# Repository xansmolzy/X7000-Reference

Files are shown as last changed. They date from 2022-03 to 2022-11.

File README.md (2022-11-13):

# X7000-Reference
Wavetek 7000 inspired voltage reference on the cheap.
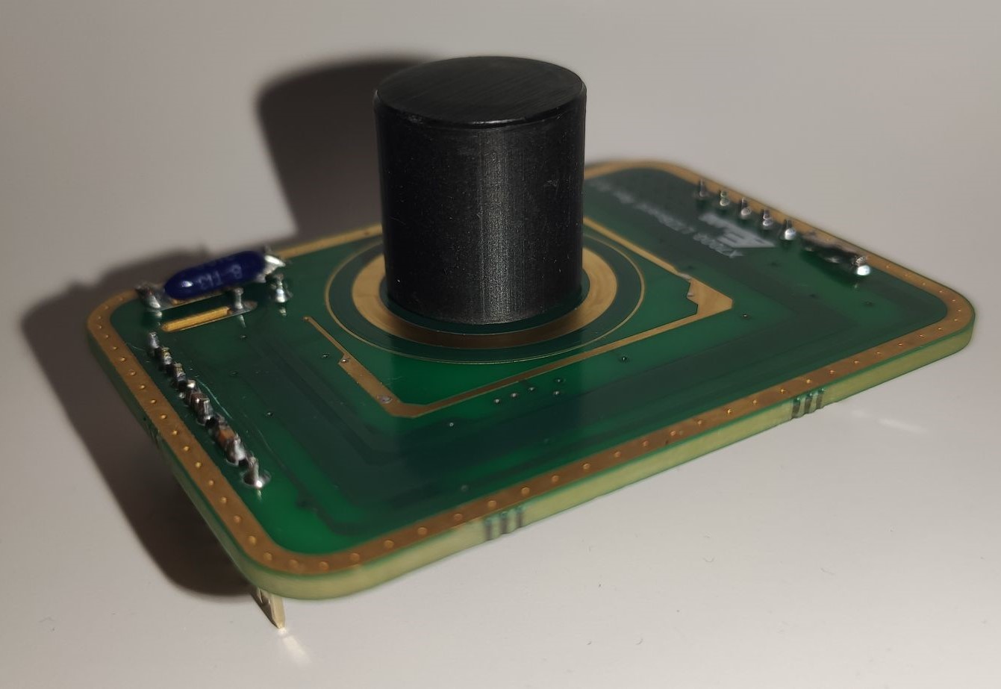
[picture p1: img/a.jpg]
Refpic1
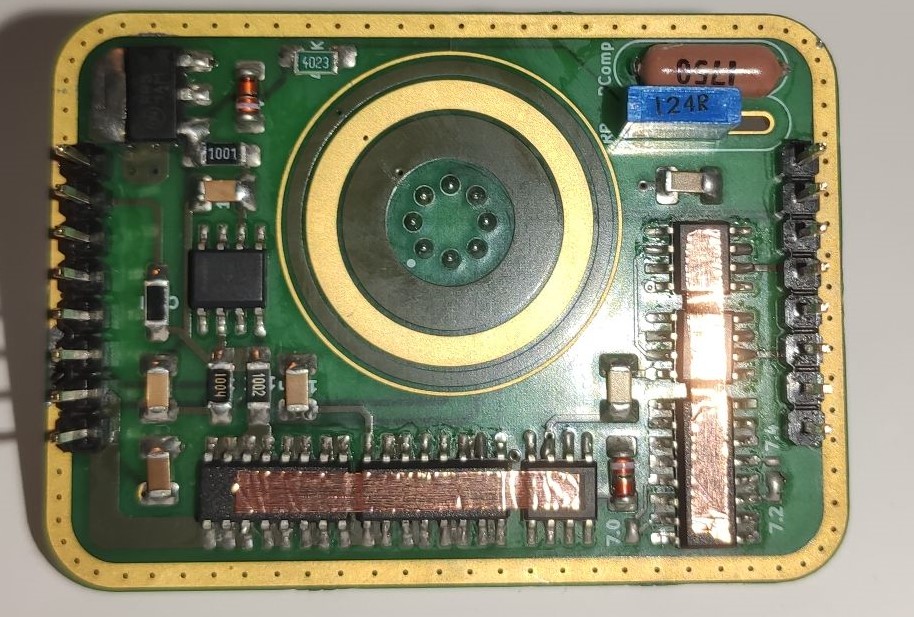
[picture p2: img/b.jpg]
Refpicé
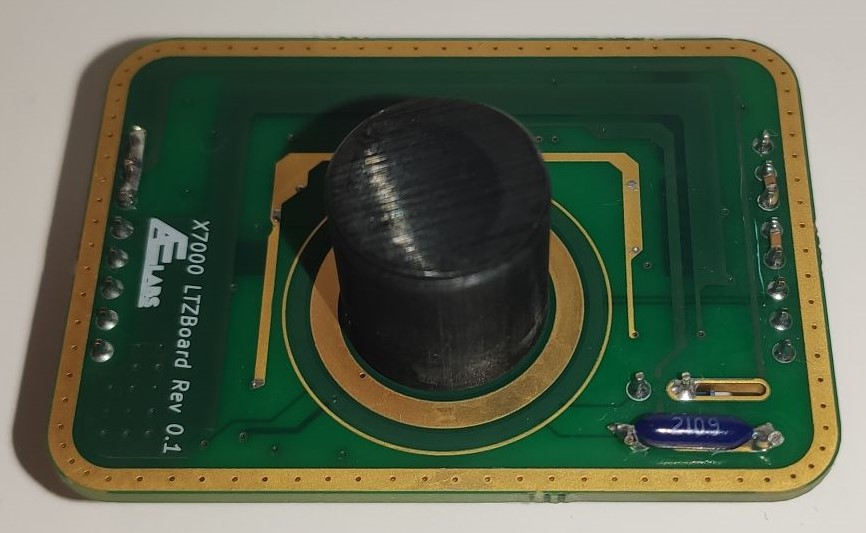
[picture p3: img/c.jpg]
Refpic3
  

## As any FOSS thing operation and specs not guaranteed
## BOM list
-  The * denounces that these parts were used in development and there is probably a better alternative.
-  **(G)** denotes this is a generic part and nearly any alternative will do.

**⚠️For V0.1 and V0.2 RCur 124Ohm and 31.2Ohm were used, based on [work](https://xdevs.com/article/b7000/) 100Ohm and 18.2Ohm are encouraged but not tested⚠️**
**⚠️LTZ-A has oscillations in the order of 100uV⚠️**

If you like to stick to tested use 124 and 31.2Ohm respectively, when V0.3 gets assembled 100 and 18.2Ohm resistors will be used and data will be provided.

| Part name          | Manufacturer      | Quantity   | Price per (eur) | Notes                                                                   |
|:-------------------|:-----------------:|:----------:|:---------------:|------------------------------------------------------------------------:|
| NOMCT16031003AT1   | Vishay            |     1      |      3,64       |                                                                         |
| NOMCT16032001AT1   | Vishay            |     2      |      3,42       |                                                                         |
|--------------------|-------------------|------------|-----------------|                                                                         |
| Y0785100R000T9L    | Vishay            |     1      |      21,53      | RCur, can be 120 for less drift with more noise, RComp needs changed    |
| PTF5621R000BYEK    | Vishay            |     1*     |      5,11       | (or better more satble resistor) RComp                                  |
| TNPW0402137RBEED   | Vishay            |     1*     |      0,67       | RComp trim to 18,18 Ohm for 100Ohms RCur                                |
|--------------------|-------------------|------------|-----------------|                                                                         |
| ADA4523-1BRZ       | Analog Devices    |     4      |      2,65       |                                                                         |
| LTZ1000CH#PBF      | Analog Devices    |     1      |      68,9       | Or LTZ1000ACH#PBF or ADR (untested)                                     |
| 1N4148UR-1         | Microchip         |     2(G)   |      0,81       |                                                                         |
| CRT1206-DY-1004ELF | Bourns            |     1(G)   |      0,35       |                                                                         |
| CRT1206-BY-1002EST | Bourns            |     1(G)   |      0,35       |                                                                         |
| CRT1206-BY-1001ELF | Bourns            |     1(G)   |      0,52       |                                                                         |
| CRT1206-BY-1002EST | Bourns            |     1(G)   |      0,35       |                                                                         |
| ERA-8AED302V       | Panasonic         |     1(G)   |      0,46       |                                                                         |
| ERA-8AEB4223V      | Panasonic         |     1(G)   |      0,58       |                                                                         |
| C1206C104K5RAC7867 | Kemet             |      4     |      0,12       |                                                                         |
| C1206X103K5RECAUT  | Kemet             |      1     |      0,44       |                                                                         |         
| 1206YC223MAT2A     | Kyocera           |      1     |      0,26       |                                                                         |
| SPZT3904T1G        | Onsemi            |      1     |      0,64       |                                                                         |
| **TOTAL**          |-------------------|------------|      1--,28     |                                                                         |

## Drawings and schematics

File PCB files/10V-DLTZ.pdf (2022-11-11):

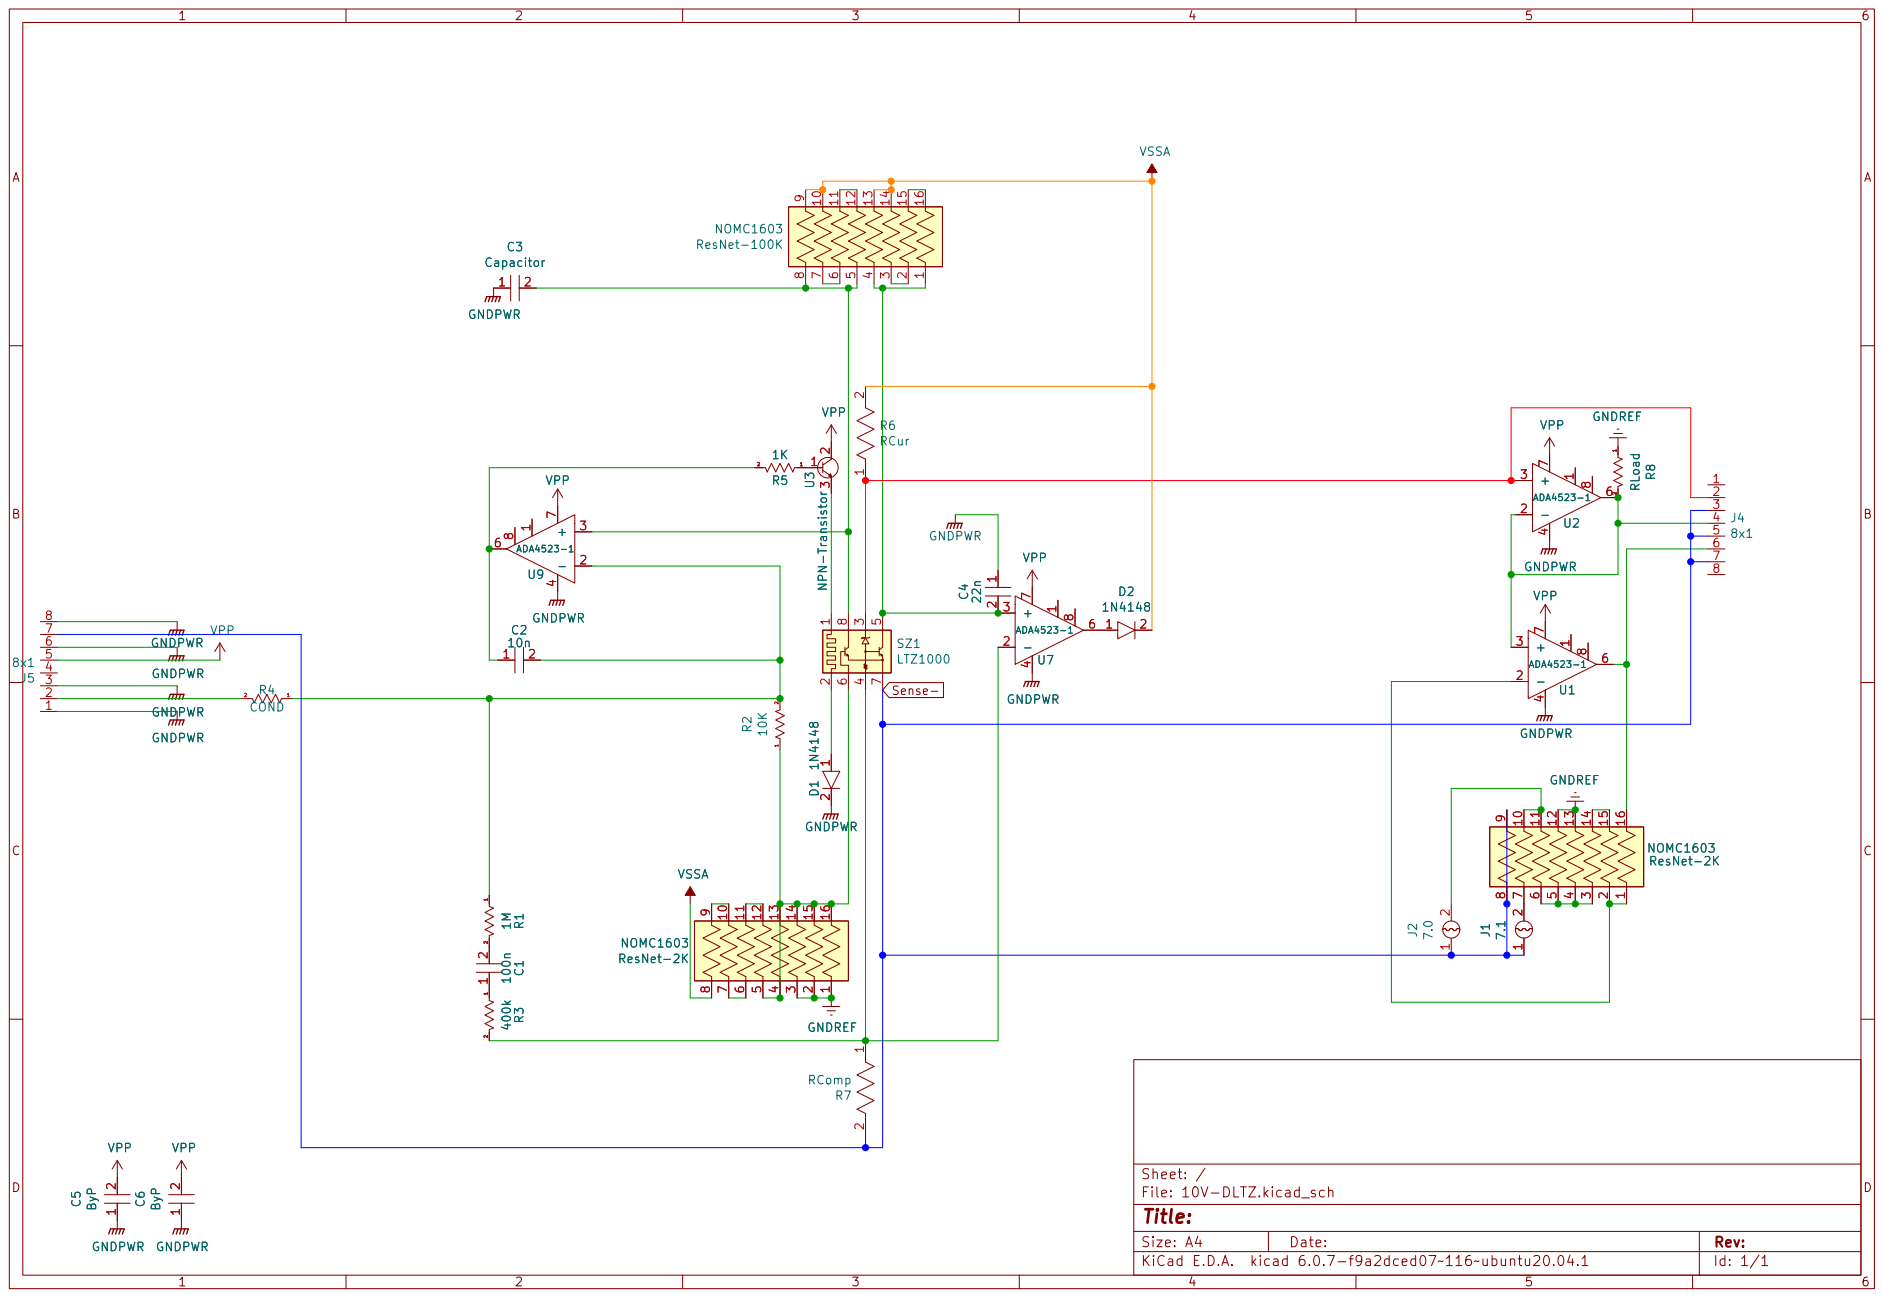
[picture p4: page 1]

8 GNDPWR GNDREF VPP GNDPWR D1 1N4148

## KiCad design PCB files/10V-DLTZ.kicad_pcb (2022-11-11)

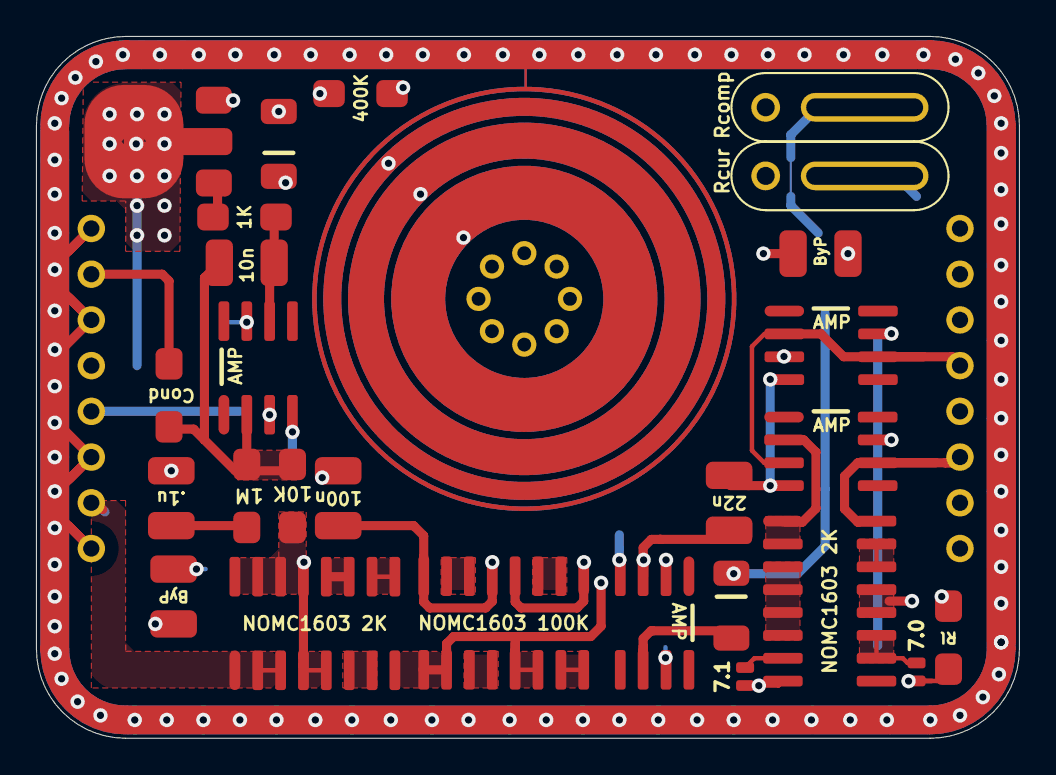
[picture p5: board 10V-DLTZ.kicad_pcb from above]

Board: 4 copper layers, 54.6 x 39.0 mm, 29 parts (0 on the bottom side), 32 nets.

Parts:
C1, C2, C3, C4, C5, C6: Capacitor; 1210
D1, D2: 1N4148
J1, J2: SolderJumper
J4, J5: 8x1; 5x1
R1, R2, R3, R4, R5, R8: RES; 1206
Rcomp: PrecRes
Rcur: PrecRes
Rn1: NOMC1603 100K; SOIC-16
Rn2: NOMC1603 2K; SOIC-16
Rn3: NOMC1603; SOIC-16
SZ1: LTZ1000; TO5-8
U1, U2, U7, U9: ADA4523-1; SOIC-8
U3: NPN-Transistor; PZT3904

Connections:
GNDPWR: C3.1, C4.1, C5.1, C6.1, D1.2, J5.1, J5.3, J5.6, J5.8, U1.4, U2.4, U7.4, U9.4
unnamed: C1.1, R3.1
unnamed: C1.2, R1.2
unnamed: C2.1, R5.2, U9.6
unnamed: C2.2, R1.1, R2.2, R4.1, U9.2
unnamed: C3.2, Rn1.5, Rn1.8, SZ1.8, U9.3
unnamed: C4.2, Rn1.1, Rn1.4, SZ1.5, U7.3
unnamed: D1.1, SZ1.2
unnamed: D2.1, U7.6
unnamed: J1.2, Rn3.7
unnamed: J2.2, Rn3.10, Rn3.11
unnamed: J4.4, R8.2, U1.3, U2.2, U2.6
unnamed: J4.6, Rn3.16, U1.6
unnamed: J5.2, R4.2
unnamed: R2.1, Rn2.4, Rn2.5, Rn2.13, Rn2.14, Rn2.15, Rn2.16, SZ1.6
unnamed: R3.2, Rcur.1, SZ1.4, U7.2
unnamed: R5.1, U3.1
unnamed: Rn1.2, Rn1.3
unnamed: Rn1.6, Rn1.7
unnamed: Rn1.11, Rn1.12
unnamed: Rn1.15, Rn1.16
unnamed: Rn2.6, Rn2.7
unnamed: Rn2.9, Rn2.10
unnamed: Rn2.11, Rn2.12
unnamed: Rn3.1, Rn3.2, U1.2
unnamed: Rn3.3, Rn3.4, Rn3.5, Rn3.6
unnamed: Rn3.14, Rn3.15
unnamed: SZ1.1, U3.3
Sense+: J4.2, Rcomp.1, SZ1.3, U2.3
Sense-: J1.1, J2.1, J4.3, J4.5, J4.7, J5.7, R8.1, Rcur.2, Rn2.1, Rn2.2, Rn2.3, Rn3.8, Rn3.9, Rn3.12, Rn3.13, SZ1.7
VPP: C5.2, C6.2, J5.5, U1.7, U2.7, U3.2, U7.7, U9.7
VSSA: D2.2, Rcomp.2, Rn1.9, Rn1.10, Rn1.13, Rn1.14, Rn2.8
